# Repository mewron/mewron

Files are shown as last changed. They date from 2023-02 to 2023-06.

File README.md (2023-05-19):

Safety considerations

In addition to the already substantial and often underappreciated dangers of building and modifying a 3D printer, which involves mains voltage wiring and manually installing and configuring hundreds of watts of electrical heating power into a small box, melt electrowriting (MEW) further introduces a high voltage hazard in the same printer. We thus ask readers to be mindful of these risks and to heed the warnings outlined in the official Voron manuals as well as the following information on safely interacting with high voltage for MEW.

Melt electrowriting requires an electrical potential in the low Kilovolt (kV) regime, and a properly designed system can achieve this easily while operating at below 10 Microamperes (μA) of current. Due to availability, the most used high voltage power supplies have a maximum output of approximately 10 kV and 1 mA, but have their maximum current output reduced to 1% (10 μA) for safe operation in case of arcing or electric shock. Since we anticipate readers to build and experiment with these machines, we ask the readers to err on the side of caution and inform themselves thoroughly based on their specific high voltage sources of the dangers and intricacies of their specific setup before they implement their ideas in practice, and consider safety interlocks, warning lights and proper signage an essential part of their experimental work.

Projet summary

This project aims to produce inexpensive, open source hardware for the scientific community, often based on designs of the Voron project or other open-source communities.
The mewron repository contains the CAD files and instructions to set up an independent extruder motor necessary for the conversion of a Voron 0.1 to a melt electrowriting (MEW) printer, the MEWron.
If you use the files in this repository for scientific work, we kindly ask you to cite the following publication that fully describes the MEWron and its capabilities:

MEWron: An open-source melt electrowriting platform

https://doi.org/10.1016/j.addma.2023.103604

Ander Reizabal, Taavet Kangur, Paula G. Saiz, Sönke Menke, Christophe Moser, Jürgen Brugger, Paul D. Dalton, Simon Luposchainsky

Additive Manufacturing, Volume 71, 2023, 103604, ISSN 2214-860.

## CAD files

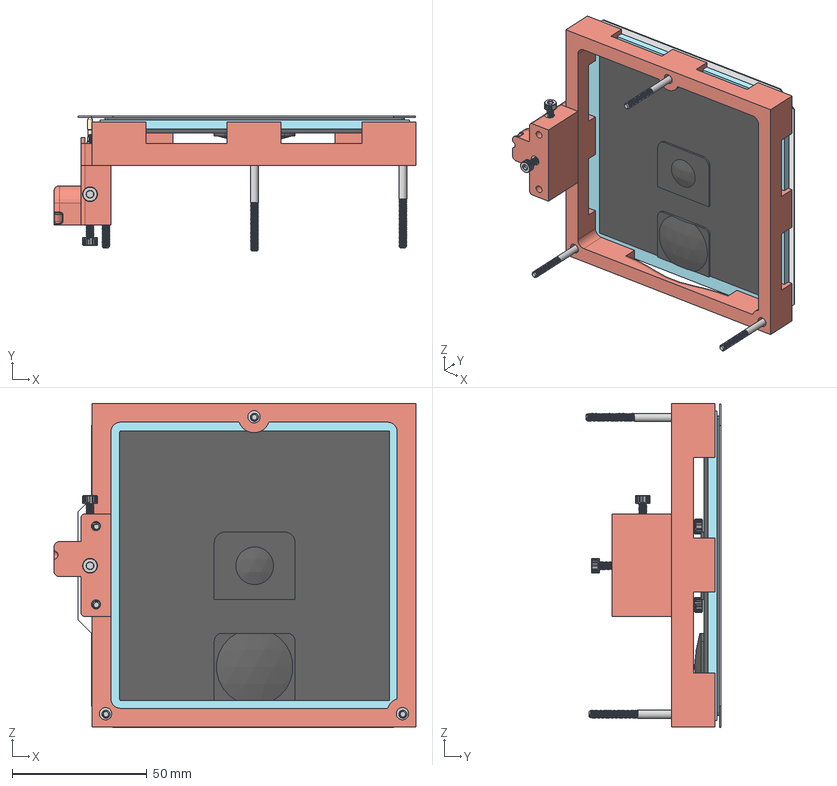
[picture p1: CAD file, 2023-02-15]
MEWron_full_assembly_MEWron_Collector v1.step
134.1 x 50.0 x 120.2 mm
Glass_Slide v0
Silicone Heat Bed 100 mm x 100 mm 24V 60W (1)
M3 Threaded Insert (2) (1) x 4
M3x14 Socket Head Screw x 4
M3x40mm Socket Head Screw x 3
Magnetic bed
Pogo-pin
Collector plate
Borosilicate Glass
HV connector (1)
Holder (1)

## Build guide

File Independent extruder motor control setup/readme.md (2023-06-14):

This folder contains the instructions and files necessary to continuously turn a stepper motor through pseudo G-code for MEW printing with Octoprint.

<font size="10"> The most recent version of this guide with updated files can be found in the appropriate sub-folder. </font>

-----

# The following requires the files from folder v1.1

Instructions V1.1 - tested with RPi_imager_1.7.5, Octoprint image octopi-1.0.0-klipper.20230222112442 and FYSETC Spyder 2.1 with Fysetc TMC2209_V3.1 stepper driver hardware.

You will need to copy files to the Raspberry Pi and access its shell/command line - we recommend PuTTY and WinSCP to accomplish this, which you should already be familiar with from the Voron manual.

•	First install and configure the printer as described in the official online Voron manual up to the 'Initial startup - stepper motor check' section. While configuring printer.cfg, it is unnecessary to configure the extruder stepper motor. 

•	Invert the Enable pin on your TMC2209 extruder stepper driver board (Instructions Figure a) and remove all jumpers for the corresponding spider motor driver socket.

•	Connect the extruder stepper motor driver pins to the raspberry PI GPIO pins (Instructions Figure b) and c)).

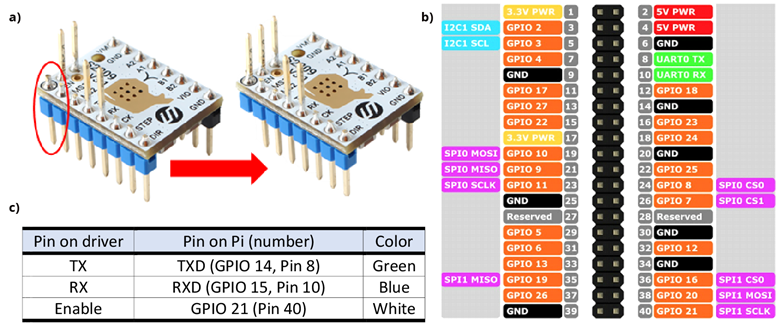
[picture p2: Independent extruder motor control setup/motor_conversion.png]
hardware modification and pin connections


•	Power up the Printer and access it through Putty

•   Input the following commands in order:

sudo apt update

sudo apt-get install python3-pip

pip3 install TMC-2209-Raspberry-Pi

sudo raspi-config

•   Navigate and select -> 3. Interface options  -> P6. Serial port  -> Login shell to be accessible over serial? -> No  -> Serial port hardware to be enabled? -> Yes  -> Finish

•   use WinSCP and copy the provided “emotor” folder in this directory on the Pi: /home/pi/scripts

•   Connect to Octoprint via the web interface and navigate to OctoPrint Settings -> Plugin Manager -> Get More -> ...from URL -> input the following two links in order:

https://github.com/vitormhenrique/OctoPrint-Enclosure/archive/master.zip

https://github.com/kantlivelong/OctoPrint-GCodeSystemCommands/archive/master.zip

•   Restart Octoprint.

•   Connect to Octoprint via the web interface and navigate to OctoPrint Settings -> GCODE System Commands

•	Press the plus sign and configure the G-Code: OCTO1 to System:

sh /home/pi/scripts/emotor/speed.sh

•   Test the command on your motor by running gcodes: OCTO1 5000 to start, OCTO1 0 to stop.

•   Finish!

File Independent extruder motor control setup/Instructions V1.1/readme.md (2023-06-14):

# Current Version 13/06/2023

Please be sure that the installation of octoprint is without klipper

On the raspbery pi installer go to <span style="color:#FF7B15 ">CHOOSE OS </span> **→** <span style="color:#FF7B15 ">Other specific-purpose OS </span> **→** <span style="color:#FF7B15 ">3D printing </span> **→** <span style="color:#FF7B15 ">OctoPi </span> **→** <span style="color:#FF7B15 ">OctoPi (stable) version 1.0.0 </span>

Instructions V1.1 - tested with: RPi_imager_1.7.5, Octoprint image octopi-1.0.0-klipper.20230222112442 and FYSETC Spyder 2.1 with Fysetc TMC2209_V3.1 stepper driver hardware.

#

You will need to copy files to the Raspberry Pi and access its shell/command line - we recommend PuTTY and WinSCP to accomplish this, which you should already be familiar with from the Voron manual.

*   First install and configure the printer as described in the official online Voron manual up to the 'Initial startup - stepper motor check' section. 
    *   While configuring printer.cfg, it is unnecessary to configure the extruder stepper motor. 
*   Invert the Enable pin on your TMC2209 extruder stepper driver board (Instructions Figure a) and remove all jumpers for the corresponding spider motor driver socket.
*   Connect the extruder stepper motor driver pins to the raspberry PI GPIO pins (Instructions Figure b) and c)).

hardware modification and pin connections

*Figure: Diagram for TMC2209 V3.1 and below Driver modification and gpio wiring*

**If you have a version 4.0 driver refer to the figure below - requires an additional 1k Ohm resistor between RX/TX**
<div style=" width:1000px">

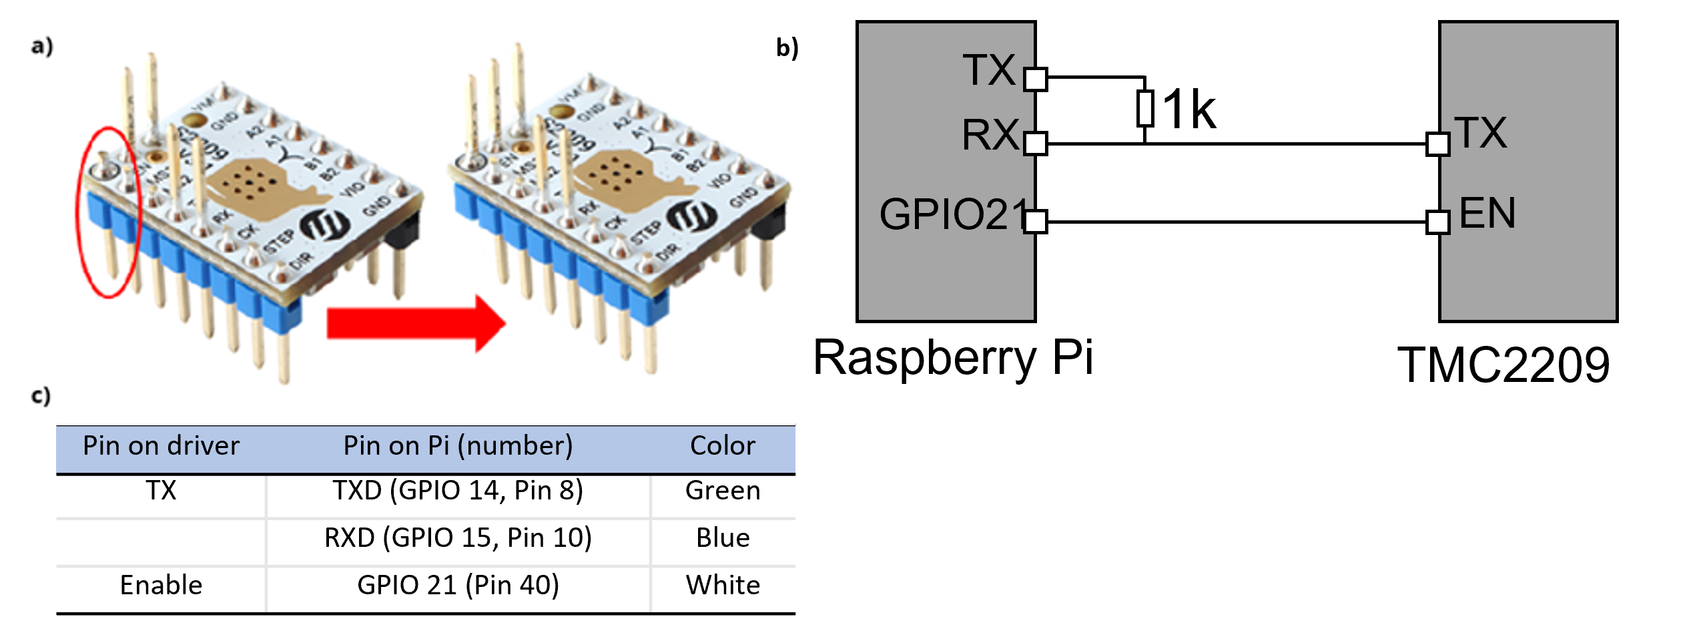
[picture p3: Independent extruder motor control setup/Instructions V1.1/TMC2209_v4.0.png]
TMC2209 V4.0


</div>

*   Power up the Printer and access it through Putty
    *   Make sure that both the raspberyr pi and computer and connected to the same wired network and then using PuTTY connect to <span style="color:#FF7B15 ">pi@octopi.local</span> 
    *   You can change the hostname of the raspberry pi in <span style="color:#FF7B15 ">raspi-config </span> **→** <span style="color:#FF7B15 ">1 System Options </span> **→** <span style="color:#FF7B15 ">S4 Hostname </span> **→** Enter your hostname (be sure to remeber this incase you loose the ip address of the raspberry pi)
*   Input the following commands in order:

````sh
pi@octopi:~$ sudo apt update

pi@octopi:~$ sudo apt-get install python3-pip

pi@octopi:~$ pip3 install TMC-2209-Raspberry-Pi

pi@octopi:~$ sudo raspi-config
````
*   Navigate and select **→** <span style="color:#FF7B15 ">3. Interface options </span> **→** <span style="color:#FF7B15 "> 6. Serial port </span> **→** <span style="color:#FF7B15 ">Login shell to be accessible over serial? </span> **→** <span style="color:#FF7B15 ">Select [No] </span> **→** <span style="color:#FF7B15 ">Serial port hardware to be enabled? </span> **→** <span style="color:#FF7B15 ">Select [Yes] </span> **→** <span style="color:#FF7B15 ">Finish </span>
    *   Be sure to restart the raspberry pi after completion of this step
*   Use WinSCP or FileZilla and copy the provided “emotor” folder in this directory on the Pi: <span style="color:#FF7B15 ">/home/pi/scripts</span>
*   Get the ip_address from the raspberry pi, this is what you will use to connect via octoprint using <span style="color:#FF7B15 ">ifconfig</span>
*   Connect to Octoprint via the web interface and navigate to <span style="color:#FF7B15 ">OctoPrint Settings</span> **→** <span style="color:#FF7B15 ">Plugin Manager</span> **→** <span style="color:#FF7B15 ">Get More</span> -> <span style="color:#FF7B15 ">...from URL</span> **→** input the following two links in order:
```
https://github.com/vitormhenrique/OctoPrint-Enclosure/archive/master.zip

https://github.com/kantlivelong/OctoPrint-GCodeSystemCommands/archive/master.zip
```

*   Restart Octoprint using the power menu.
*   Connect to Octoprint via the web interface and navigate to <span style="color:#FF7B15 ">OctoPrint Settings</span> **→** <span style="color:#FF7B15 ">GCODE System Commands</span>
*   Press the plus sign and configure the G-Code: OCTO1 to System:
```
sh /home/pi/scripts/emotor/speed.sh
```
*   Test the command on your motor by running gcodes: OCTO1 5000 to start, OCTO1 0 to stop.

# Finish!

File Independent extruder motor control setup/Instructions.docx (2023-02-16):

INSTRUCTIONS FOR INDEPENDENT EXTRUDER MOTOR CONTROL

You will need to copy files to the Raspberry Pi and access its shell/command line - we recommend PuTTY and WinSCP to accomplish this, which you should already be familiar with from the Voron manual. In the following instructions, all console commands are written in cursive font.

- First install and configure the printer as described in the official online manual up to the 'Initial startup - stepper motor check' section. While configuring printer.cfg, it is unnecessary to configure the extruder stepper motor.
- Disconnect the Printer from power.
- Invert the Enable pin on your TMC2209 extruder stepper driver board (Instructions Figure 1a) and remove all jumpers for the corresponding spider motor driver socket.
- Connect the extruder stepper motor driver pins to the raspberry PI GPIO pins (Instructions Figure 1b and c):

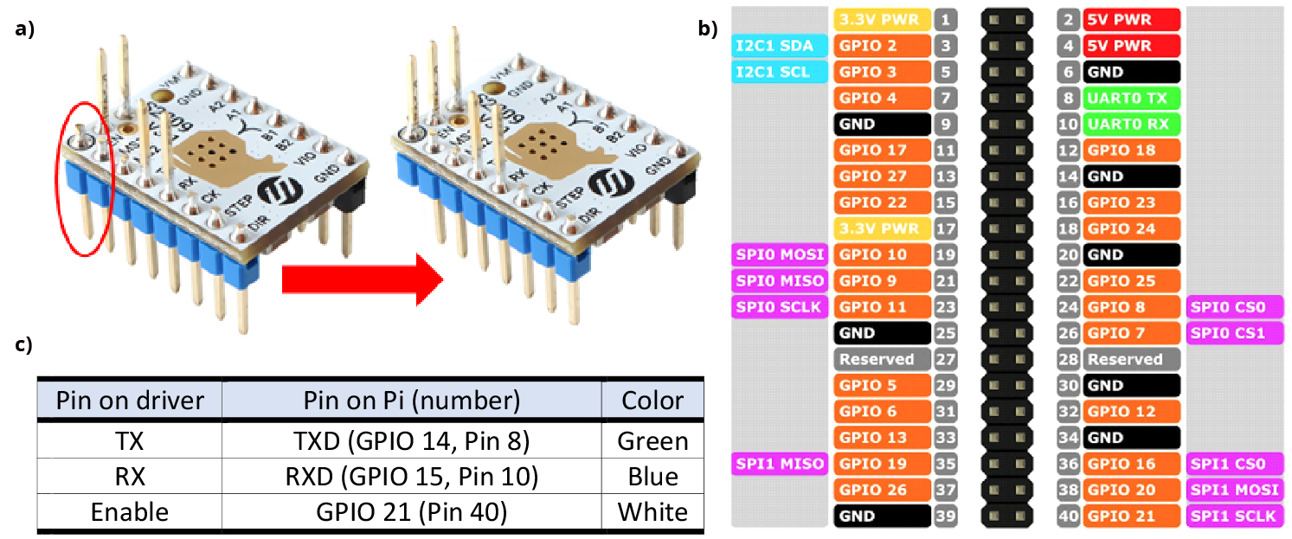
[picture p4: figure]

Instructions Figure 1. a) Example of extruder stepper driver board inversion, b) raspberry PI GPIO pins resume, c) summary of stepper motor driver pins to the raspberry PI GPIO connections.

- Power up the Printer and access it through Putty
- Install and update software packages by executing the following commands:
- sudo apt update
- sudo apt full-upgrade
- sudo apt-get install python3-pip
- pip3 install TMC-2209-Raspberry-Pi
- pip3 install bitstring
- sudo pip3 install gpiozero
- Install the following Octoprint plugins by executing the following two commands (ignore line breaks!)
- /home/pi/oprint/bin/python3 -m pip --disable-pip-version-check install https://github.com/vitormhenrique/OctoPrint-Enclosure/archive/master.zip --no-cache-dir
- /home/pi/oprint/bin/python3 -m pip --disable-pip-version-check install https://github.com/kantlivelong/OctoPrint-GCodeSystemCommands/archive/master.zip --no-cache-dir
- Enable passwordless sudo for the pi user:
- sudo nano /etc/sudoers
- Navigate to the line “# includedir /etc/sudoers.d” and write the following statement in the next line, then save and exit nano:
- pi ALL=(ALL) NOPASSWD: ALL
- Enable serial port:
- sudo raspi-config
- (Navigate and select -> 3. Interface options -> P6. Serial port -> Login shell to be accessible over serial? -> No -> Serial port hardware to be enabled? -> Yes -> Finish)
- Install missing features:
- sudo apt-get install python3-pip
- sudo pip3 install gpiozero
- use WinSCP and copy the provided “emotor” folder in this directory on the Pi: /home/pi/scripts
- use WinSCP to copy the following files to the same emotor folder:
- The TMC2209_Raspberry_Pi Library (Located in: /home/pi)
- The src folder inside the TMC2209_Raspberry_Pi Library
- The bitstring.py file (Located in: /home/pi/oprint/lib/python3.7/site-packages)
- The serial folder (Located in: /home/pi/oprint/lib/python3.7/site-packages)
- The RPi folder (Located in: /home/pi/oprint/lib/python3.7/site-packages)
- Connect to the printer via Octoprint, and navitage to settings -> GCODE system commands
- Press the plus sign and configure the G-Code: OCTO1 to System:
- sh /home/pi/scripts/emotor/speed.sh
- Test the command by running gcodes: OCTO1 10000 to start, OCTO1 0 to stop.
- Finish

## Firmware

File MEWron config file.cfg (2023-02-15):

## Voron Design MEWron 0.1 Spider TMC2209 UART config

## *** THINGS TO CHANGE/CHECK: ***
## MCU paths							          [mcu] section
## Thermistor types						      [extruder] and [heater_bed] sections - See 'sensor types' list at end of file
## Z Endstop Switch location	      [safe_z_home] section
## Homing end position				      [gcode_macro G32] section
## Z Endstop Switch  offset for Z0	[stepper_z] section
## Probe points							        [quad_gantry_level] section
## Min & Max gantry corner postions	[quad_gantry_level] section
## PID tune								          [extruder] and [heater_bed] sections
## Fine tune E steps					      [extruder] section

[mcu]
##	Obtain definition by "ls -l /dev/serial/by-id/" 
##--------------------------------------------------------------------
serial: /dev/serial/by-id/usb-Klipper_XXXXXXXXXXXXXXXXXXXXXXXXXXXXXXXXX

## Uncomment below if you're using the Raspberry uart0 to communicate with Spider
#restart_method: command

[printer]
kinematics: corexy
max_velocity: 200  
max_accel: 2000		        
max_z_velocity: 15			#Max 15 for 12V TMC Drivers, can increase for 24V
max_z_accel: 45
square_corner_velocity: 6.0

#####################################################################
#      X/Y Stepper Settings
#####################################################################

[stepper_x]
##	Connected to X-MOT (B Motor)
step_pin: PE11
dir_pin: !PE10
enable_pin: !PE9
rotation_distance: 40
microsteps: 32
full_steps_per_rotation:200  #set to 400 for 0.9 degree stepper
endstop_pin: ^PB14
position_min: 0
position_endstop: 114
position_max: 120
homing_speed: 50   #Max 100
homing_retract_dist: 5
homing_positive_dir: true

##	Make sure to update below for your relevant driver (2208 or 2209)
[tmc2209 stepper_x]
uart_pin: PE7
interpolate: False
run_current: 0.5
sense_resistor: 0.110
stealthchop_threshold: 0

[stepper_y]
##	Connected to Y-MOT (A Motor)
step_pin: PD8
dir_pin: !PB12
enable_pin: !PD9
rotation_distance: 40
microsteps: 32
full_steps_per_rotation:200  #set to 400 for 0.9 degree stepper
endstop_pin: ^PB13
position_min: 0
position_endstop: 114
position_max: 120
homing_speed: 50   #Max 100
homing_retract_dist: 5
homing_positive_dir: true

##	Make sure to update below for your relevant driver (2208 or 2209)
[tmc2209 stepper_y]
uart_pin: PE15
interpolate: False
run_current: 0.5
sense_resistor: 0.110
stealthchop_threshold: 0

#####################################################################
#   Z Stepper Settings
#####################################################################

## In Z-MOT Position
## Z0 Stepper - Front Left
[stepper_z]
step_pin: PD14
dir_pin: PD13
enable_pin: !PD15
rotation_distance: 40
gear_ratio: 80:16
microsteps: 32
##  In Z- Position
endstop_pin: ^PA0
##  Z-position of nozzle (in mm) to z-endstop trigger point relative to print surface (Z0)
##  (+) value = endstop above Z0, (-) value = endstop below
##	Increasing position_endstop brings nozzle closer to the bed
##  After you run Z_ENDSTOP_CALIBRATE, position_endstop will be stored at the very end of your config
position_endstop: 2.3 #I make it manually and remove the Z endstop calibration
position_max: 100
position_min: -5 #0 before
homing_speed: 10
second_homing_speed: 3
homing_retract_dist: 3

## we can try to remove this next part or change if there are problems
##	Make sure to update below for your relevant driver (2208 or 2209)
[tmc2209 stepper_z]
uart_pin: PD10
interpolate: False
run_current: 0.4 
sense_resistor: 0.110
stealthchop_threshold: 0

##	In E1-MOT Position
##	Z1 Stepper - Rear Left
#[stepper_z1]
#step_pin: PE6
#dir_pin: !PC13
#enable_pin: !PE5
#rotation_distance: 40
#gear_ratio: 80:16
#microsteps: 32

##	Make sure to update below for your relevant driver (2208 or 2209)
#[tmc2209 stepper_z1]
#uart_pin: PC14
#interpolate: False
#run_current: 0.8
#sense_resistor: 0.110
#stealthchop_threshold: 0

##	In E2-MOT Position
##	Z2 Stepper - Rear Right
#[stepper_z2]
#step_pin: PE2
#dir_pin: PE4
#enable_pin: !PE3
#rotation_distance: 40
#gear_ratio: 80:16
#microsteps: 32

##	Make sure to update below for your relevant driver (2208 or 2209)
#[tmc2209 stepper_z2]
#uart_pin: PC15
#interpolate: False
#run_current: 0.8
#sense_resistor: 0.110
#stealthchop_threshold: 0

##	In E3-MOT Position
##	Z3 Stepper - Front Right
#[stepper_z3]
#step_pin: PD12
#dir_pin: !PC4
#enable_pin: !PE8
#rotation_distance: 40
#gear_ratio: 80:16
#microsteps: 32

#[tmc2209 stepper_z3]
#uart_pin: PA15
#interpolate: False
#run_current: 0.8
#sense_resistor: 0.110
#stealthchop_threshold: 0

#####################################################################
#   Extruder
#####################################################################

##	In E0-MOT Position
[extruder]
step_pin: PD5
dir_pin: PD6
enable_pin: !PD4

##	Update value below when you perform extruder calibration
##	If you ask for 100mm of filament, but in reality it is 98mm:
##	rotation_distance = <previous_rotation_distance> * <actual_extrude_distance> / 100
##  22.6789511 is a good starting point for Bondtech 5mm gears
rotation_distance: 20.41105599	#Bondtech 5mm Drive Gears
gear_ratio: 50:10				#BMG Gear Ratio. FOR MINI AFTERBURNER 50:10 
microsteps: 16
full_steps_per_rotation: 200	#200 for 1.8 degree, 400 for 0.9 degree
nozzle_diameter: 0.400
filament_diameter: 1.75
##    Printhead heater.  In E0 OUT Position
heater_pin: PB15
##	thermistor. In TE0 position
sensor_type: NTC 100K beta 3950
sensor_pin: PC0
min_temp: 10
max_temp: 270
max_power: 1.0
min_extrude_temp: 170
#control = pid
#pid_kp = 26.213
#pid_ki = 1.304
#pid_kd = 131.721

##	Try to keep pressure_advance below 1.0
#pressure_advance: 0.05
##	Default is 0.040, leave stock
#pressure_advance_smooth_time: 0.040

##	In E0-MOT Position
##	Make sure to update below for your relevant driver (2208 or 2209)
[tmc2209 extruder]
uart_pin: PD7
interpolate: true
run_current: 0.3
sense_resistor: 0.110
stealthchop_threshold: 0

[verify_heater extruder]
max_error: 1000 #Change to around 300 for the last calibration
check_gain_time: 300 #Change to around 120 for the last calibration
hysteresis: 5
heating_gain: 2


#####################################################################
#   Bed Heater
#####################################################################
[heater_bed]
##	SSR Pin - In BED OUT position
heater_pin: PB4
sensor_type: NTC 100K beta 3950
sensor_pin: PC3
##	Adjust Max Power so your heater doesn't warp your bed
max_power: 0.6
min_temp: 0
max_temp: 120
#control: pid
#pid_kp: 58.437
#pid_ki: 2.347
#pid_kd: 363.769

#####################################################################
#	Fan Control
#####################################################################

[heater_fan hotend_fan]
##	Hotend Fan - FAN0 Connector
pin: PB0
max_power: 1.0
#kick_start_time: 0.5
heater: extruder
heater_temp: 80
##	If you are experiencing back flow, you can reduce fan_speed
#fan_speed: 1.0

[fan]
##	Print Cooling Fans - FAN1 Connector
pin: PB1
max_power: 1.0
#kick_start_time: 0.5        ##	Depending on your fan, you may need to increase this value
##	if your fan will not start. Can change cycle_time (increase)
##	if your fan is not able to slow down effectively
off_below: 0.2
cycle_time: 0.01

#####################################################################
#	Homing and Gantry Adjustment Routines
#####################################################################

[idle_timeout]
timeout: 3600
#This time mark the time when the printer temperature shut down if i am not printing (for security)
#The default value is 1800 but you can increase it for more heating times before start to print

[safe_z_home]
home_xy_position: 114,114
speed: 50.0
z_hop: 5

## To be used with BED_SCREWS_ADJUST
[bed_screws]
screw1: 60,5
screw1_name: front screw
screw2: 5,115
screw2_name: back left
screw3: 115,115
screw3_name: back right

#####################################################################
#	Macros
#####################################################################

[gcode_macro PRINT_START]
#   Use PRINT_START for the slicer starting script - please customize for your slicer of choice
gcode:
    G28                            ; home all axes
    G1 Z20 F3000                   ; move nozzle away from bed
   
[gcode_macro PRINT_END]
#   Use PRINT_END for the slicer ending script - please customize for your slicer of choice
gcode:
    M400                           ; wait for buffer to clear
    G92 E0                         ; zero the extruder
    G1 E-4.0 F3600                 ; retract filament
    G91                            ; relative positioning

    #   Get Boundaries
    {% set max_x = printer.configfile.config["stepper_x"]["position_max"]|float %}
    {% set max_y = printer.configfile.config["stepper_y"]["position_max"]|float %}
    {% set max_z = printer.configfile.config["stepper_z"]["position_max"]|float %}

    #   Check end position to determine safe direction to move
    {% if printer.toolhead.position.x < (max_x - 20) %}
        {% set x_safe = 20.0 %}
    {% else %}
        {% set x_safe = -20.0 %}
    {% endif %}

    {% if printer.toolhead.position.y < (max_y - 20) %}
        {% set y_safe = 20.0 %}
    {% else %}
        {% set y_safe = -20.0 %}
    {% endif %}

    {% if printer.toolhead.position.z < (max_z - 2) %}
        {% set z_safe = 2.0 %}
    {% else %}
        {% set z_safe = max_z - printer.toolhead.position.z %}
    {% endif %}

    G0 Z{z_safe} F3600             ; move nozzle up
    G0 X{x_safe} Y{y_safe} F20000  ; move nozzle to remove stringing
    TURN_OFF_HEATERS
    M107                           ; turn off fan
    G90                            ; absolute positioning
    G0 X60 Y{max_y} F3600          ; park nozzle at rear
	
[gcode_macro LOAD_FILAMENT]
gcode:
   M83                            ; set extruder to relative
   G1 E30 F300                    ; load
   G1 E15 F150                    ; prime nozzle with filament
   M82                            ; set extruder to absolute
    
[gcode_macro UNLOAD_FILAMENT]
gcode:
   M83                            ; set extruder to relative
   G1 E10 F300                    ; extrude a little to soften tip
   G1 E-40 F1800                  ; retract some, but not too much or it will jam
   M82                            ; set extruder to absolute

#*# <---------------------- SAVE_CONFIG ---------------------->
#*# DO NOT EDIT THIS BLOCK OR BELOW. The contents are auto-generated.
#*#
#*# [heater_bed]
#*# control = pid
#*# pid_kp = 37.086
#*# pid_ki = 1.261
#*# pid_kd = 272.584
#*#
#*# [extruder]
#*# control = pid
#*# pid_kp = 29.707
#*# pid_ki = 0.231
#*# pid_kd = 954.714
